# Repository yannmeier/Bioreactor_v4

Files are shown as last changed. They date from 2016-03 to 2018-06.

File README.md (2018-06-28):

# Bioreactor_v4

This repository is dedicated to the version 4 of the Bioreactor.

## Electronics

The architecture for v4 is articulated around one central board powered by 
an ATmega32u4 MCU relying on nilRTOS and external boards for interfacing
to extra sensors and/or LCD screeens.

The main board comes with the following features:
- stepper motor control with Neodimium magnet
- Load cell based on HX711
- PID heater control
- DS18B20+ temperature sensing
- LoRaWAN mid-range wireless communication
- 2 peristaltic pumps control
- SPI port to control a slave LCD board
- 2 I2C ports for master to slave communication to external modules
- Serial over USB
- 12V DC jack supply

There are already a few external extra modules:
- LCD SPI slave board on ATmega32u4
- pH & Conductommetry regulation I2C slave, also works as a stand alone (in development phase)
- gas flux and mix control with analogic valves, also works as a stand alone (in development phase)
- spectrophotometer immersed in the bioreactor, also works as a stand alone (in development phase)

References:
-https://www.arduino.cc/en/Main/ArduinoBoardLeonardo
-https://github.com/greiman/NilRTOS-Arduino

Revision notes:
Bioreactor V4.2:
- Changed operating frequency from 16MHz to 8MHz
- Changed operating voltage from 5V to 3.3V
- Removed 5V regulation
- Routed LoRa RST pin to MCU with additionnal pull-up
- Hack to be performed on hardware (D6<>D12) for software compatibility
Bioreactor V4.3:
- Stepper motor has individually controllable phases
- LoRa SMA PCB edge Antenna support
- Hack to be performed on hardware (D6<>D12) for software compatibility
Bioreactor V4.4:
- D6<>D12 exchanged to provide PWM PID control of the heater

## Mechanics

(Documentation coming soon)

#Bioreactor_v5

In parallel to the development of the version 4 of the Bioreactor, a version 5, relying on the 
more powerful SAMD21 (Cortex M0+ ARM) MCU and FreeRTOS is currently being studied.

References:
-https://www.arduino.cc/en/Main/ArduinoBoardZero
-http://www.freertos.org/Atmel_SAMD20_RTOS.html
-https://www.kickstarter.com/projects/rabidprototypes/neutrino-the-tiny-32-bit-arduino-zero-compatible/updates

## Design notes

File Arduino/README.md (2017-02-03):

# Installation

## Cloning the project

You know with age we take some habits and it would be easier if you follow the same one ...

All our github projects are always in a folder called `git`
that is at the first level of the home directory. It is followed by the 
name of the github user/organisation and finaly the project.

So to install the project from bash:
```
mkdir -p ~/git/bioreactor/
cd ~/git/bioreactor/
git clone git@github.com:Bioreactor/Bioreactor_v4.git
```

The possiblity to clone the project will require that you have validate your public key
in github !

## Installing the Arduino IDE

Currently we are still using the Arduino IDE. Plase download the last 1.6 version
of the program from: https://www.arduino.cc/en/Main/Software

## Another IDE ...

Ready to try a new IDE to program the Arduino ? Have a look at this eclipse project and install it:
http://eclipse.baeyens.it/

Once it works, start the program, select the Arduino Leonardo and go in the menu `Arduino` -> `New sketch`.
As project name just enter 'BioMain' and for the location: `~/git/bioreactor/Bioreactor_v4/Arduino/BioMain`

After don't select any template (just normal .ino files that are already in the folder). The program
will automatically import the libraries if there are placed correctly (see just after).

## Hardware support for Leonardo 8MHz = Lilipad Arduino USB

The version 4.2 of the bioreactor is opeerating at 8MHz/3V3 instead of the standard 16MHz/5V.
In order to have the correct boadloader just use Lilipad Arduino USB as board.

If you do any mistake and try to pretend it is a normal Leonardo, you will be able to flash the program but the USB port will not be recognized. You will have to reflash the bootleader !!!```

## Using USBtiny
By default the last version of Fedora will only give you a USB readonly access and will prevent to burn the board loader.
In order for the USBTiny to have r/w access you should add a USB rules:
```
# UDEV rule for Arduino ISP R3 programmer board,
# to prevent having to run Arduino IDE as root to get it to program.
# Copy this file to /etc/udev/rules.d so

SUBSYSTEMS=="usb", ATTRS{idVendor}=="1781", ATTRS{idProduct}=="0c9f", GROUP="plugdev", MODE="0666"

```

## Libraries

In this project we use many non standard libraries. By default the Arduino IDE
will look for them in `~/Arduino/libraries`

If you are using only our project it is easier to directly point this folder
to the libraries that are present in the github. 

```
mkdir ~/Arduino/
ln -s ~/git/bioreactor/Bioreactor_v4/Arduino/libraries/ ~/Arduino/
```
Attention: Time library update v1.5.0 change commited in BioMain including TimeLib.h instead of Time.h resolves bugs on OSX 

## That's it

You should now be able to compile the project from the Arduino IDE.
You can now proceed burning the bootloader using the Leonardo 8MHz newly created option and upload your code selecting the same Leonardo 8MHz in the list of available MCUs from the IDE. To do so, you must select the Leonardo 8MHz board under /Tools/Boards/ in the Arduino IDE or selecting the proper device during project creation in Eclipse. Note that the LCD board works under 16MHz/5V and must be flashed as a standard Leonardo board not a 8MHz one. You must also select the right board version when programming the board via USB !

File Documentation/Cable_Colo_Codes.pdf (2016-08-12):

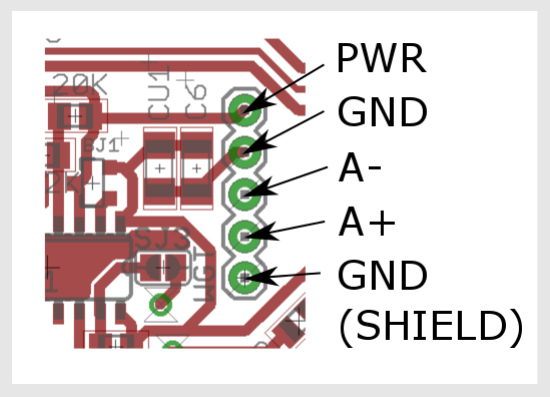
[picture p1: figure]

SENSOR
1 red | PWR (N$5)
2 black | GND
3 white | A-
4 green | A+
5 | GND (Shield)

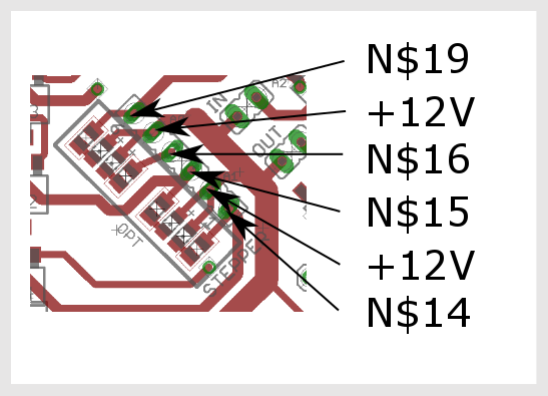
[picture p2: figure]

MOTOR
1 red | N$14
2 black | +12V
3 white | N$15
4 green | N$16
5 blue | +12V
6 yellow | N$19

## Color codes

## Load cells

MOTHERBOARD

## Stepper

MOTHERBOARD

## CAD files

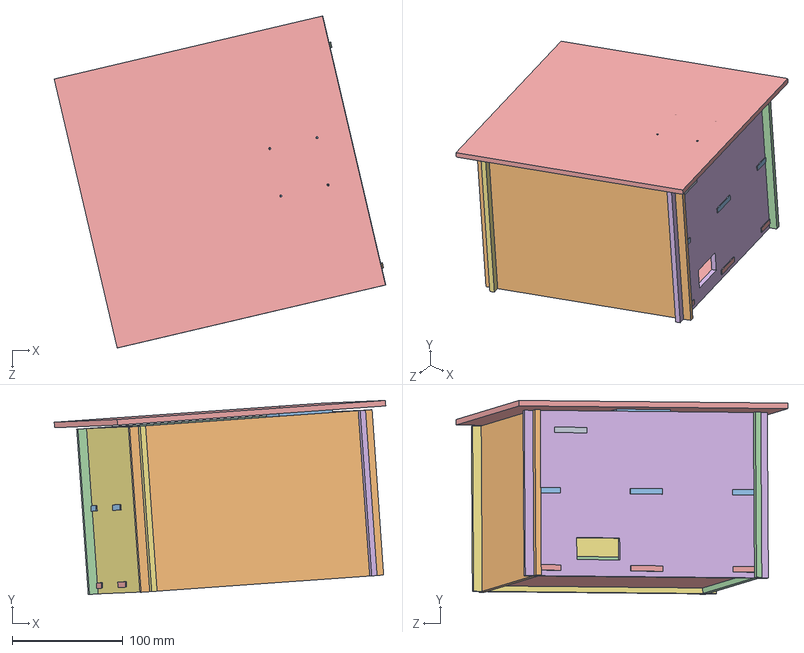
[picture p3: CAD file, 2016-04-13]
CAD/Assembly.SLDASM
300.1 x 175.7 x 300.5 mm
weight sensor
Stepper 33
middle face
Arduino
bottom face
lateral face - hole
lateral face
back support weight sensor x 2
support weight sensor
back face
support plateau
magnet support

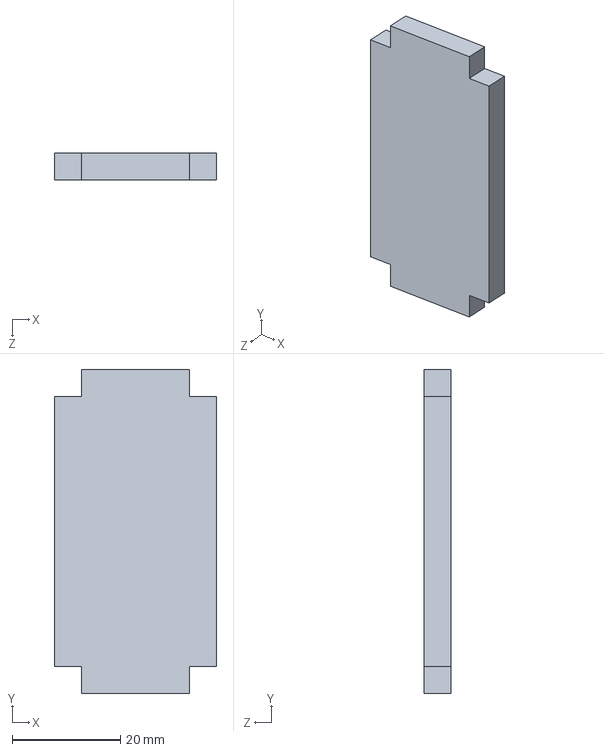
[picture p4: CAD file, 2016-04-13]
CAD/back support weight sensor.SLDPRT
30.0 x 60.0 x 5.00 mm

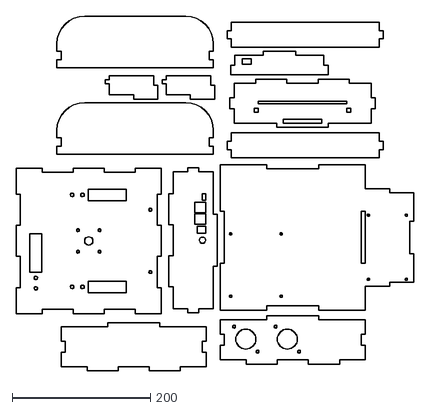
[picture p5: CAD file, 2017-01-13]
CAD/v4.3/DXF/Bioreacteur_v4_6mm.dxf
575.0 x 513.0

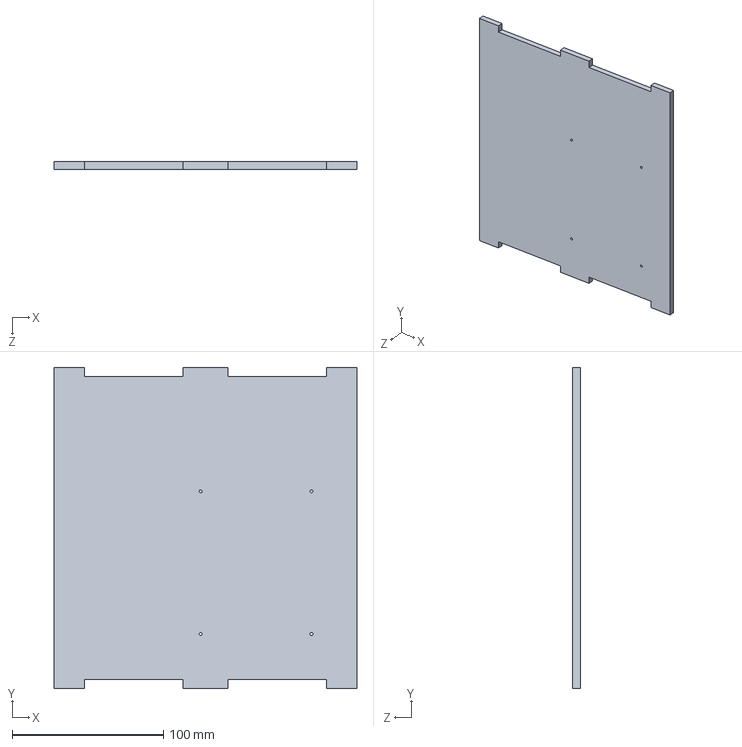
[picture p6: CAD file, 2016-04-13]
CAD/bottom face.SLDPRT
200.0 x 212.0 x 5.00 mm

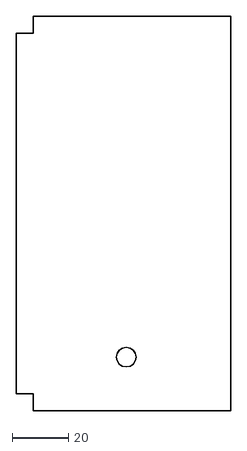
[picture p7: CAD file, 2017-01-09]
CAD/v4.3/DXF/Bioreacteur_v4_4mm.dxf
76.0 x 140.0

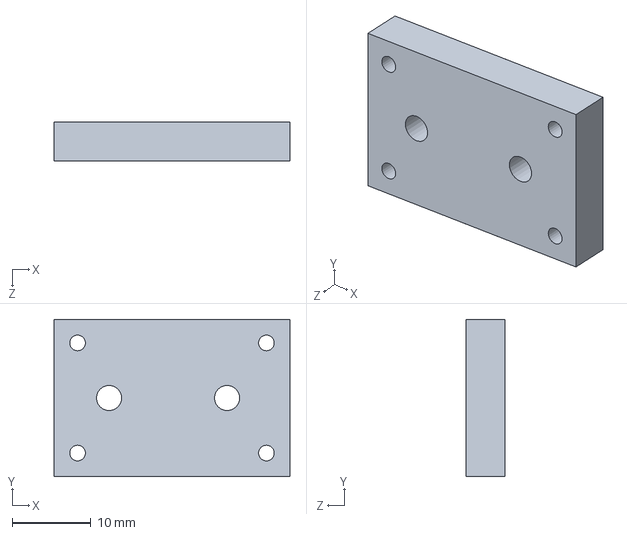
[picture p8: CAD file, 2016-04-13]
CAD/support plateau.SLDPRT
30.0 x 20.0 x 5.00 mm

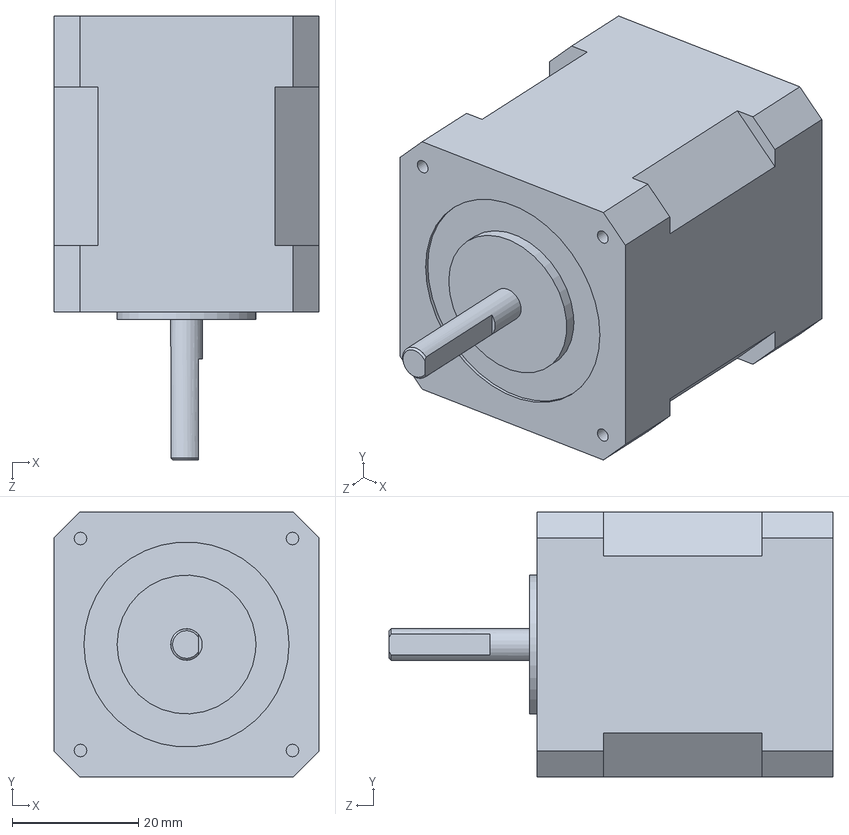
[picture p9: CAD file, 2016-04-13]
CAD/Stepper 47.SLDPRT
42.0 x 42.0 x 70.3 mm

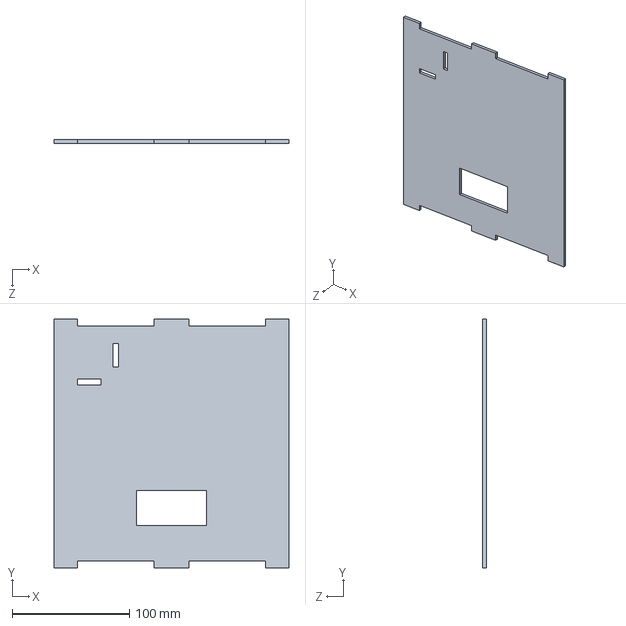
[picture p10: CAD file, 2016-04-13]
CAD/middle face.SLDPRT
200.0 x 212.0 x 3.00 mm

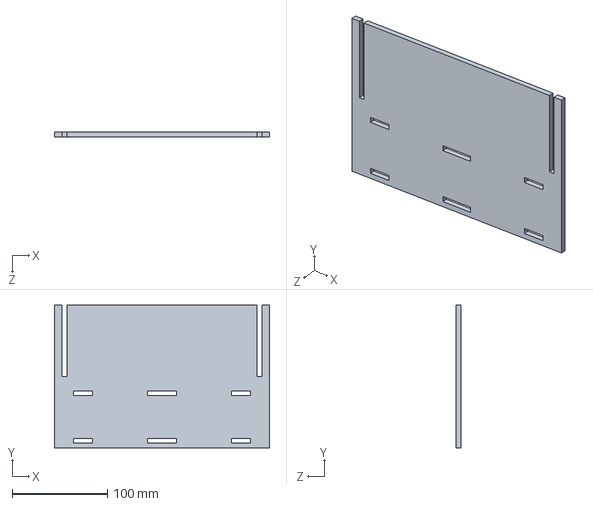
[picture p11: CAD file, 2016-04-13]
CAD/side face.SLDPRT
226.0 x 150.0 x 5.00 mm

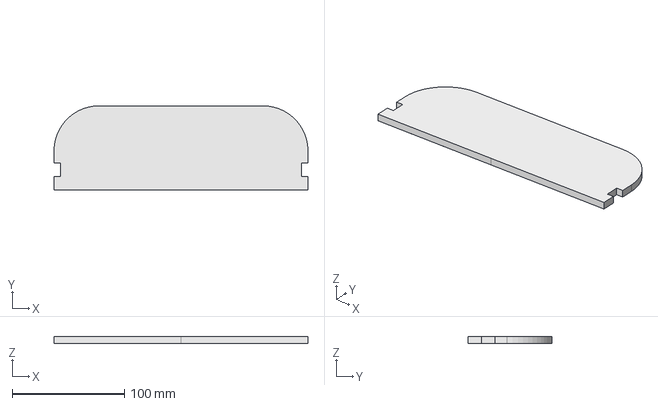
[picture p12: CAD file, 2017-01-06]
CAD/v4.3/BASE_JUPE_MALE.fcstd
226.0 x 75.0 x 6.00 mm

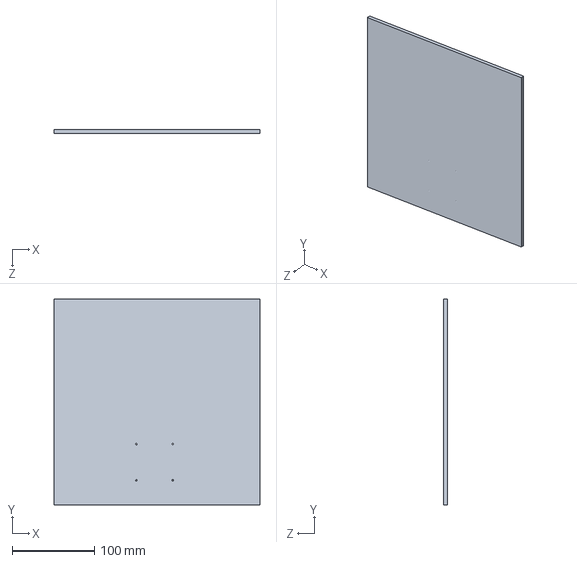
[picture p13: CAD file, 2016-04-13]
CAD/top face.SLDPRT
250.0 x 250.0 x 5.00 mm

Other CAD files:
CAD/v4.3/Tank_alu_foundation.FCStd
CAD/v4.3/Bioreactor_sketches_04.fcstd
CAD/v4.3/Bioreactor_sketches_03.fcstd
CAD/v4.3/Bioreactor_sketches.fcstd
CAD/v4.3/Bioreactor_sketches_02.fcstd
CAD/Arduino.SLDPRT
CAD/Stepper 33.SLDPRT
CAD/back face.SLDPRT
CAD/front face.SLDPRT
CAD/lateral face - hole.SLDPRT
CAD/lateral face.SLDPRT
CAD/magnet support.SLDPRT
CAD/support weight sensor.SLDPRT
CAD/v4.0_old/back face.SLDPRT
CAD/v4.0_old/front face.SLDPRT
CAD/v4.0_old/lateral face - hole.SLDPRT
CAD/v4.0_old/lateral face.SLDPRT
CAD/v4.0_old/magnet support.SLDPRT
CAD/v4.0_old/support weight sensor.SLDPRT
CAD/v4.1/A Bioreactor v3.SLDASM
CAD/v4.1/A screen.SLDASM
CAD/v4.1/Box Board v1.4.stl
CAD/v4.1/Foot.SLDPRT
CAD/v4.1/Pump support v1.2 .stl
CAD/v4.1/Pump support.SLDPRT
CAD/v4.1/Screen support v1.1.SLDPRT
CAD/v4.1/Screen support v1.1.stl
CAD/v4.1/Screen support.STL
CAD/v4.1/Support v3.1.SLDPRT
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

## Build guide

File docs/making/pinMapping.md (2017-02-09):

Pin mapping
===========

Port | Pin | Arduino Mask | Bertha V4.1-2 | Bertha V4.3 | Bertha V4.4 | pH V5.x | LCD V0.2/V1.x
-----|-----|--------------|---------------|-------------|-------------|---------|---------------
B | 0 | RXLED/SS | RXLED | RXLED | RXLED | RXLED | SS
B | 1 | SCK | SCK | SCK | SCK | SCK | SCK
B | 2 | MOSI | MOSI | MOSI | MOSI | MOSI | MOSI
B | 3 | MISO | MISO | MISO | MISO | MISO | MISO
B | 4 | D8 | - | Stepper 1 | Stepper 1 | Stepper#1-1 | LCD #11
B | 5 | D9 | - | Stepper 2 | Stepper 2 |  | LCD #6
B | 6 | D10 | SPI flash slave | SPI flash slave | PWM food IN | SPI flash slave | LCD #4
B | 7 | D11 | SPI LCD slave | SPI LCD slave | SPI LCD slave | SPI LCD slave | -
C | 6 | D5 | LoRa RST | LoRa RST | PWM food OUT | LoRa RST | -
C | 7 | D13 | Blink Led | Blink Led | Blink Led | Blink Led | Blink Led
D | 0 | D3/SCL | I2C SCL | I2C SCL | I2C SCL | I2C SCL | -
D | 1 | D2/SDA | I2C SDA | I2C SDA | I2C SDA | I2C SDA | -
D | 2 | D0/RX | LoRa RX | LoRa RX | LoRa RX | LoRa RX | ENC B
D | 3 | D1/TX | LoRa TX | LoRa TX | LoRa TX | LoRa TX | ENC A
D | 4 | D4/A6 | Ext. OneWire | Ext. OneWire | Ext. OneWire | Stepper#1-2 | LCD #14
D | 5 | TXLED | TXLED | TXLED | TXLED | TXLED | -
D | 6 | D12 | PID (hack: D12<>D6) | PID (hack: D12<>D6) | OneWire | Stepper#1-3 | LCD #13
D | 7 | D6 | OneWire (hack: D6<>D12) | OneWire (hack: D6<>D12) | PID on PWM | Stepper#1-4 | LCD #12
E | 2 | D7 | - | - | - | Data HX711 | ENCODER INT
E | 6 | HWB | HWB | HWB | HWB | HWB | HWB
F | 0 | A5 | SCK HX711 | SCK HX711 | SCK HX711 | SCK HX711 | -
F | 1 | A4 | Data HX711 | Data HX711 | Data HX711 | PH NTC TEMP | -
F | 4 | A3 | Food out | Food out | SPI flash slave | Stepper#2-4 | -
F | 5 | A2 | Food in | Food in | LoRa RST | Stepper#2-1 | -
F | 6 | A1 | Stepper 2+4 | Stepper 4 | Stepper 4 | Stepper#2-2 | -
F | 7 | A0 | Stepper 1+3 | Stepper 3 | Stepper 3 | Stepper#2-3 | -

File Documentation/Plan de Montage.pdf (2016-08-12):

# PLAN DE MONTAGE

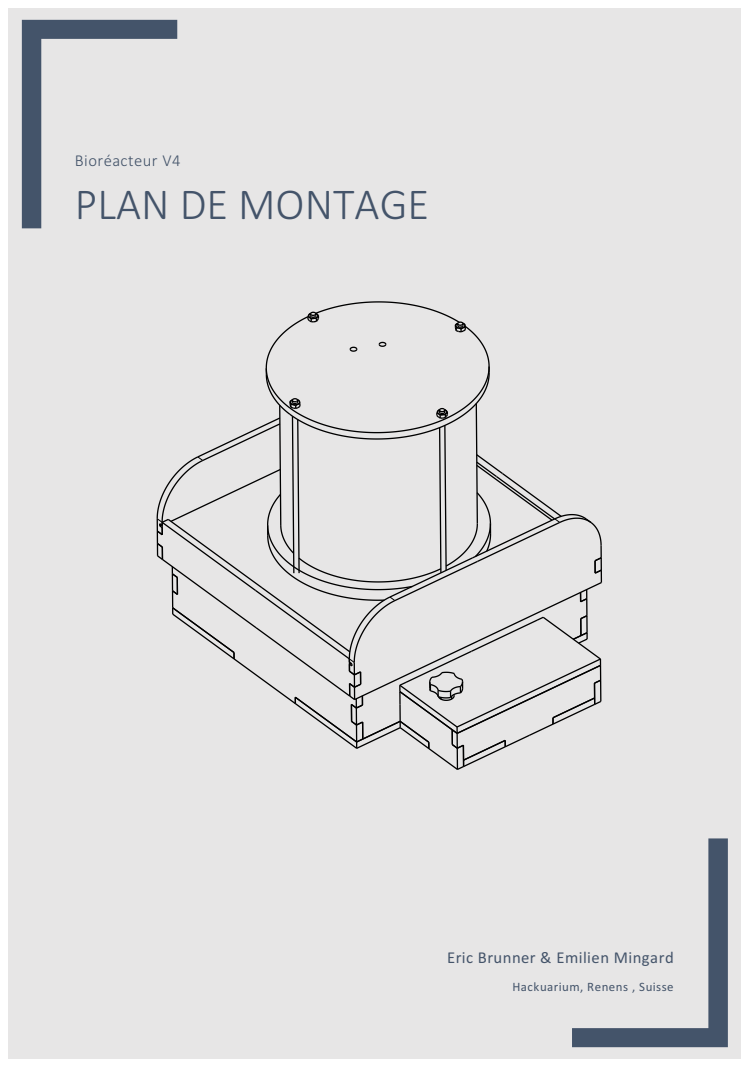
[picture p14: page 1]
Bioréacteur V4

Eric Brunner & Emilien Mingard

Hackuarium, Renens , Suisse

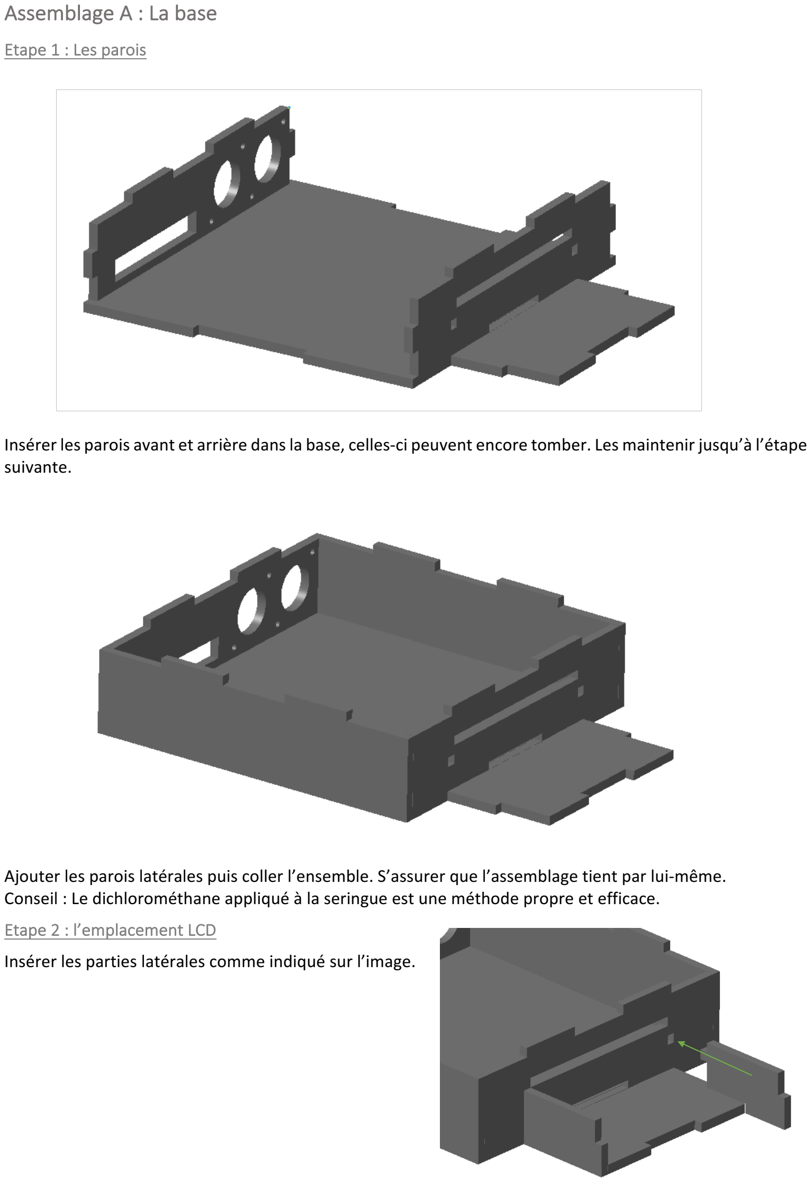
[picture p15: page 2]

### Assemblage A : La base

Etape 1 : Les parois

Insérer les parois avant et arrière dans la base, celles-ci peuvent encore tomber. Les maintenir jusqu’à l’étape suivante.

Ajouter les parois latérales puis coller l’ensemble. S’assurer que l’assemblage tient par lui-même. Conseil : Le dichlorométhane appliqué à la seringue est une méthode propre et efficace.
Etape 2 : l’emplacement LCD
Insérer les parties latérales comme indiqué sur l’image.

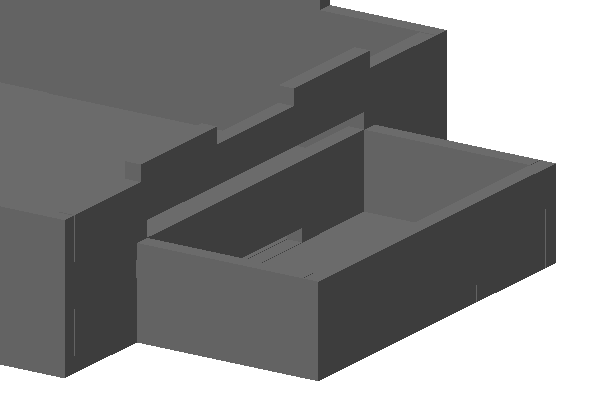
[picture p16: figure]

Déposer la partie centrale pour compléter l’espace puis coller avec de la colle. Conseil : Voir étape 1.
Etape 3 : Installation des composants électroniques et mécaniques

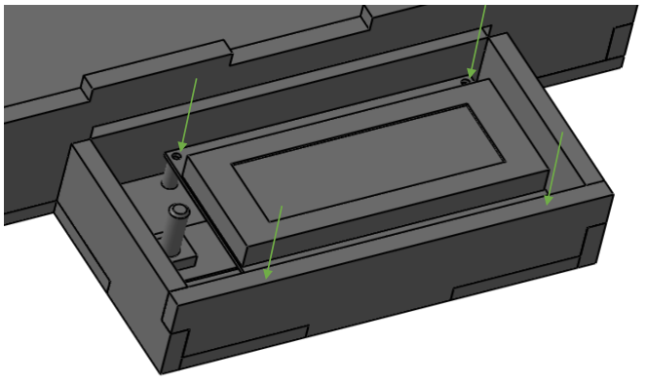
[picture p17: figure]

Visser l’écran LCD dans son emplacement, celui-ci s’appuie sur 4 entretoises 14mm. Pièces standards : 4 x M3x20.

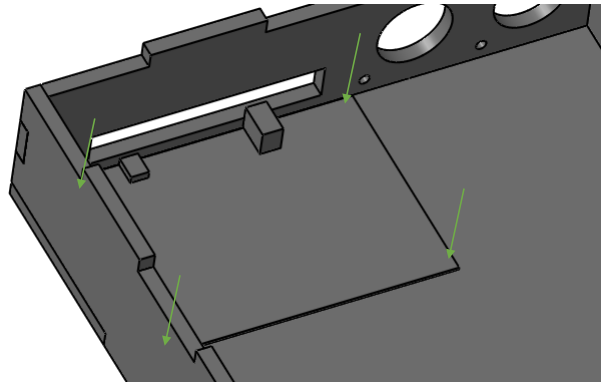
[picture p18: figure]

Visser la carte mère en face de l’ouverture prévue sur la partie arrière, les ports doivent être visibles de l’extérieur. Des entretoises de 4mm sont nécessaires.
Pièces standards : 4 x M3x10 (Solution économe : 4 x M3x20 avec entretoises supplémentaires).

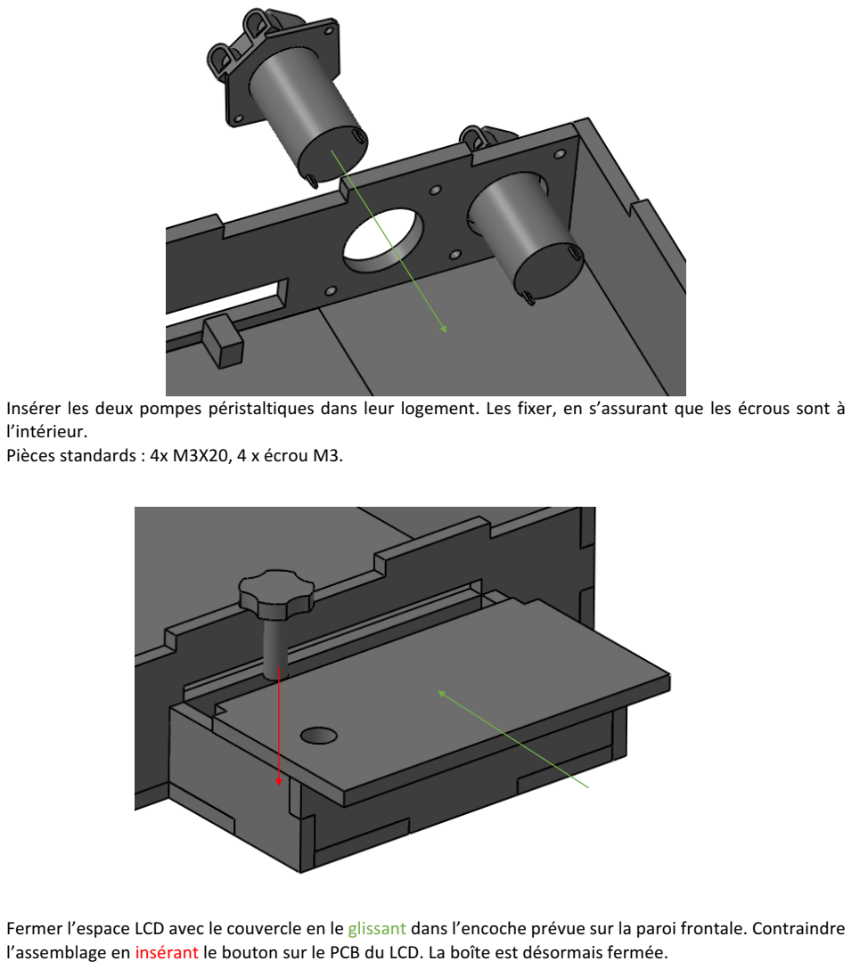
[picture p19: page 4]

Insérer les deux pompes péristaltiques dans leur logement. Les fixer, en s’assurant que les écrous sont à l’intérieur.
Pièces standards : 4x M3X20, 4 x écrou M3.

Fermer l’espace LCD avec le couvercle en le glissant dans l’encoche prévue sur la paroi frontale. Contraindre l’assemblage en insérant le bouton sur le PCB du LCD. La boîte est désormais fermée.

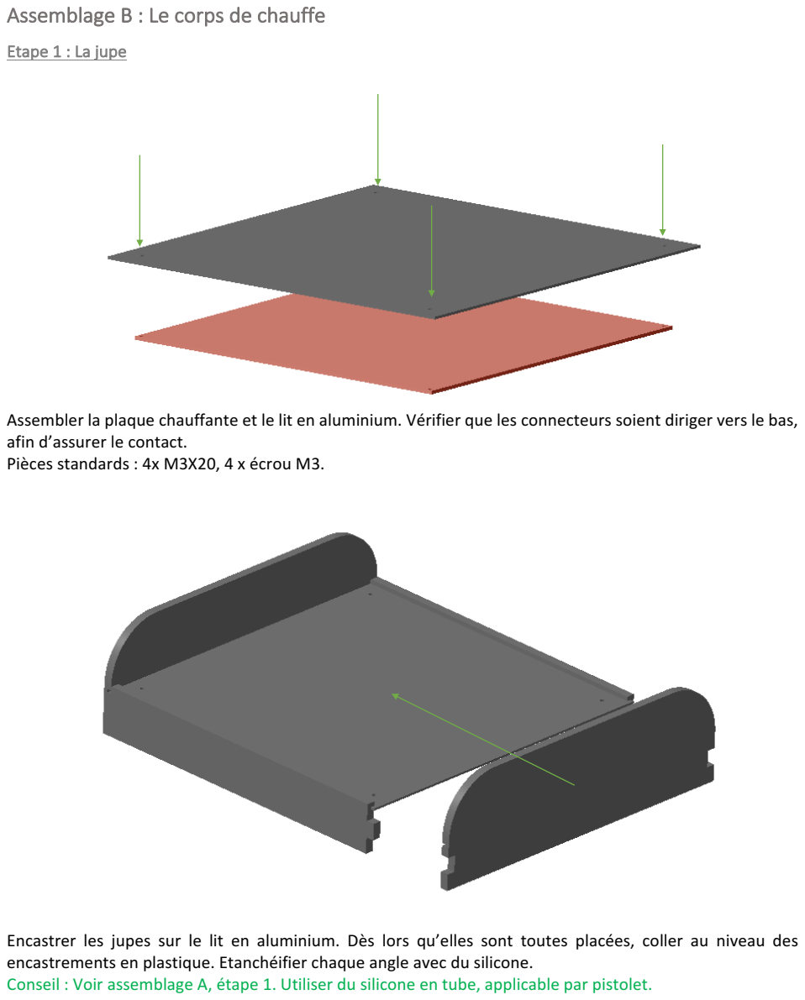
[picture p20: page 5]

### Assemblage B : Le corps de chauffe

Etape 1 : La jupe

Assembler la plaque chauffante et le lit en aluminium. Vérifier que les connecteurs soient diriger vers le bas, afin d’assurer le contact.
Pièces standards : 4x M3X20, 4 x écrou M3.

Encastrer les jupes sur le lit en aluminium. Dès lors qu’elles sont toutes placées, coller au niveau des encastrements en plastique. Etanchéifier chaque angle avec du silicone.
Conseil : Voir assemblage A, étape 1. Utiliser du silicone en tube, applicable par pistolet.

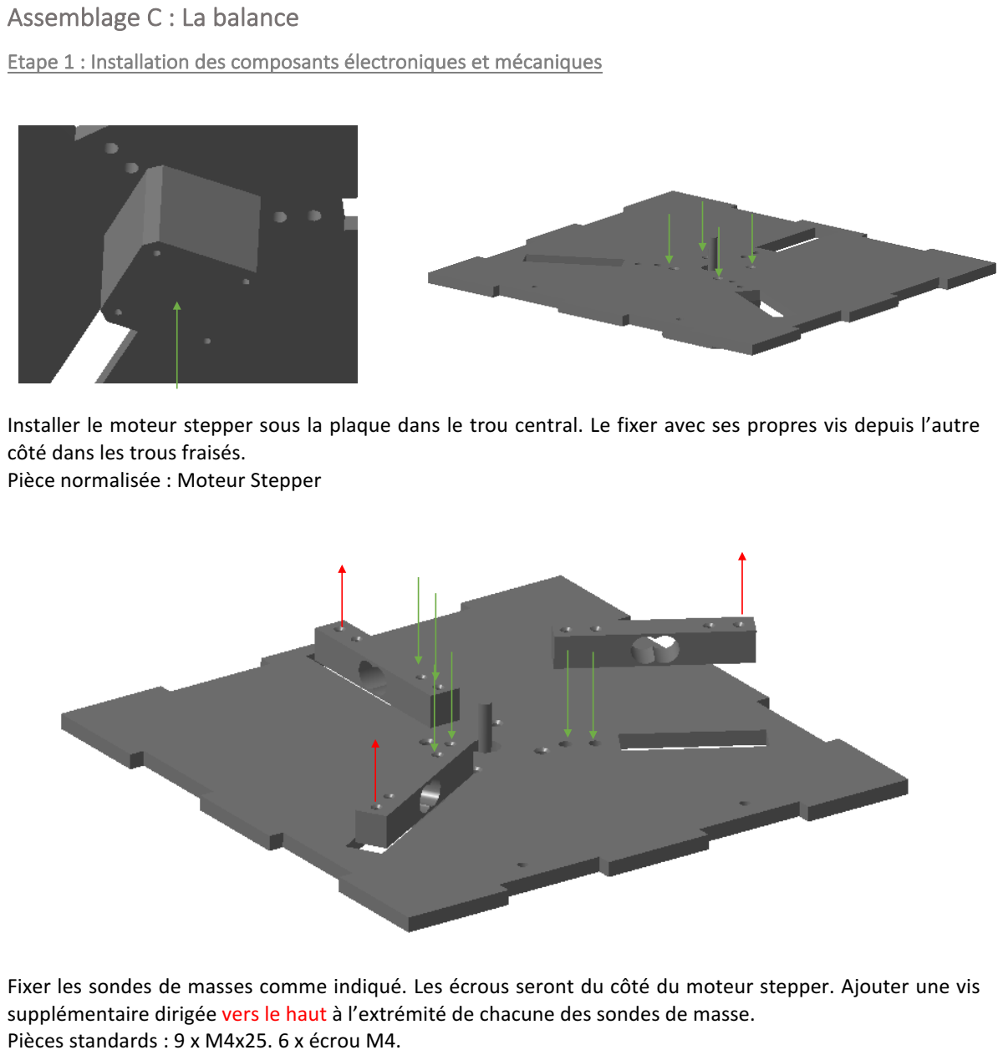
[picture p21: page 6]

### Assemblage C : La balance

Etape 1 : Installation des composants électroniques et mécaniques

Installer le moteur stepper sous la plaque dans le trou central. Le fixer avec ses propres vis depuis l’autre côté dans les trous fraisés.
Pièce normalisée : Moteur Stepper

Fixer les sondes de masses comme indiqué. Les écrous seront du côté du moteur stepper. Ajouter une vis supplémentaire dirigée vers le haut à l’extrémité de chacune des sondes de masse.
Pièces standards : 9 x M4x25. 6 x écrou M4.

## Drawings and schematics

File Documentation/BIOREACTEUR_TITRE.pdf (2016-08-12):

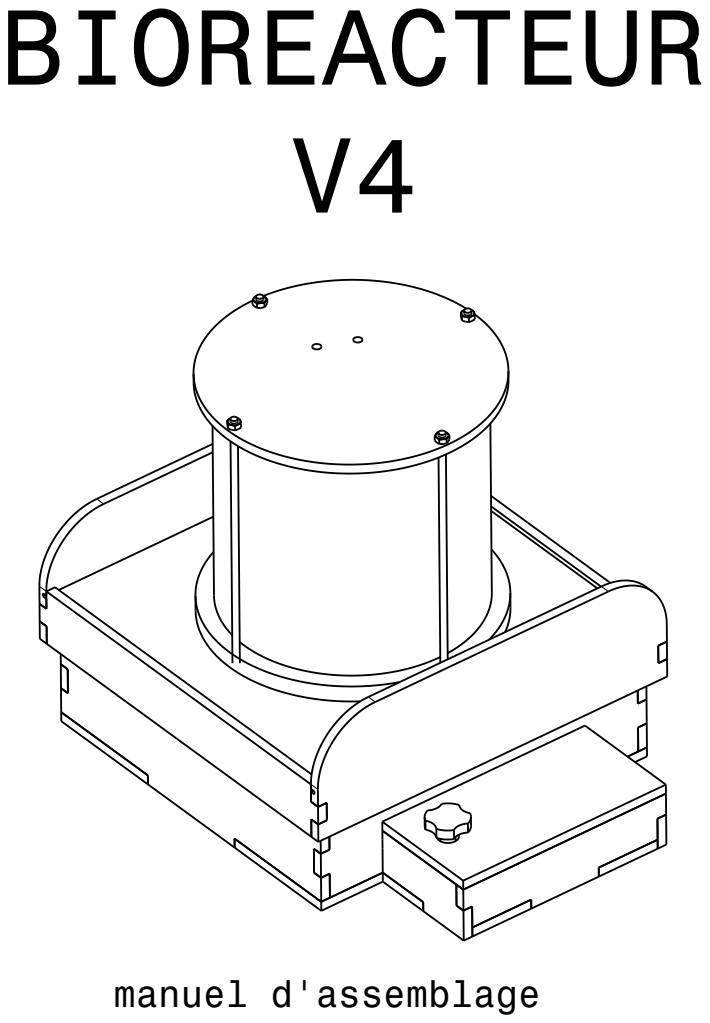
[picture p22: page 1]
manuel d'assemblage

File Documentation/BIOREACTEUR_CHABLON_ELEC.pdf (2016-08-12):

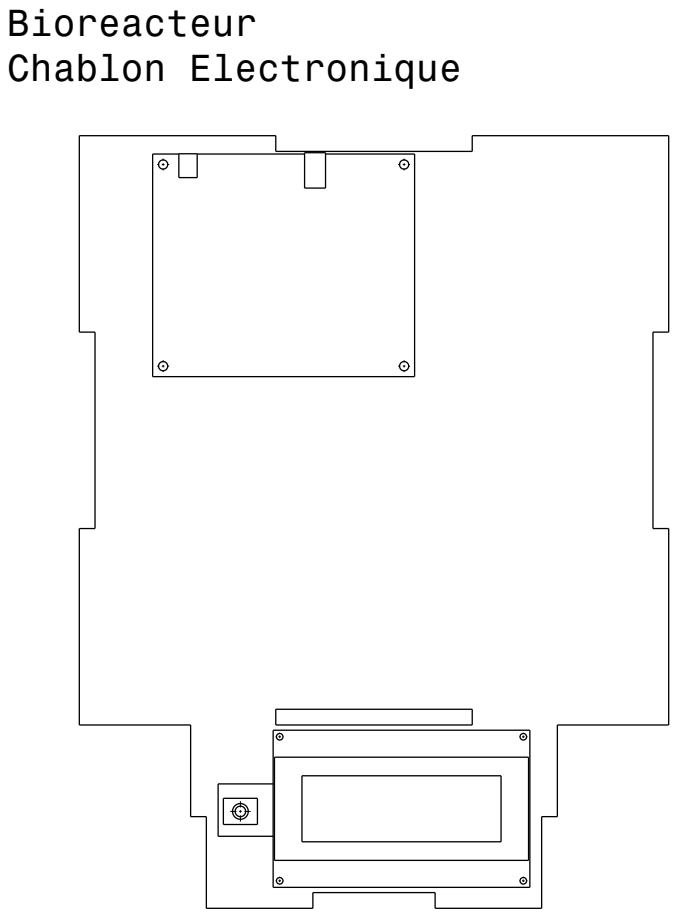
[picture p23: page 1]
Chablon Electronique

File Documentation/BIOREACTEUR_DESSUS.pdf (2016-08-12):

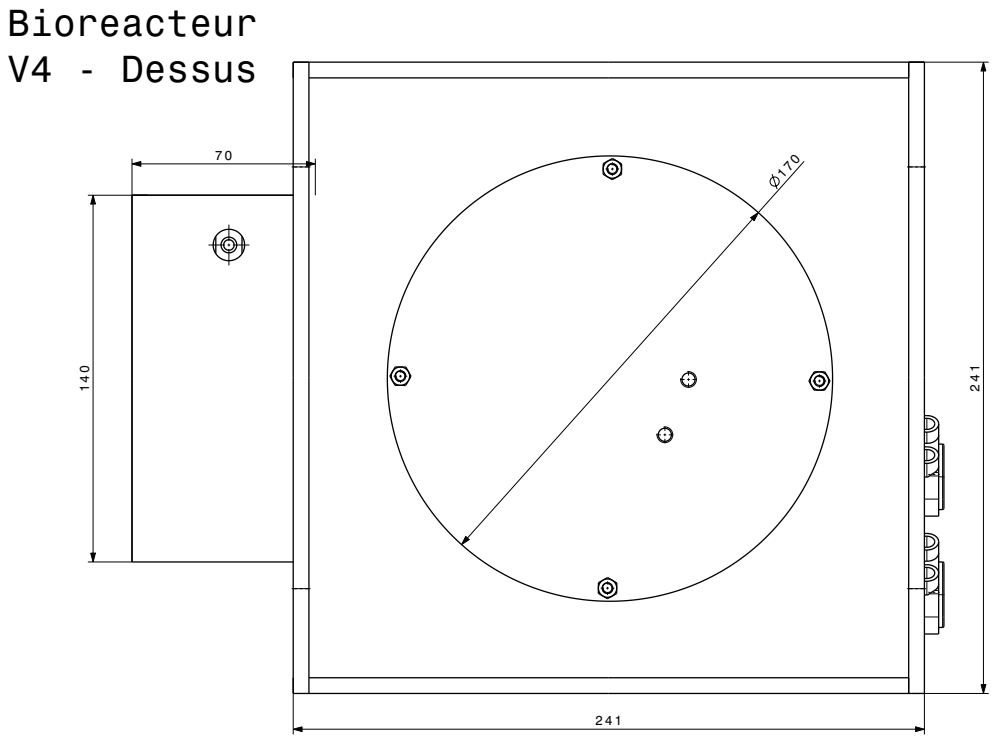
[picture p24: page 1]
V4 - Dessus

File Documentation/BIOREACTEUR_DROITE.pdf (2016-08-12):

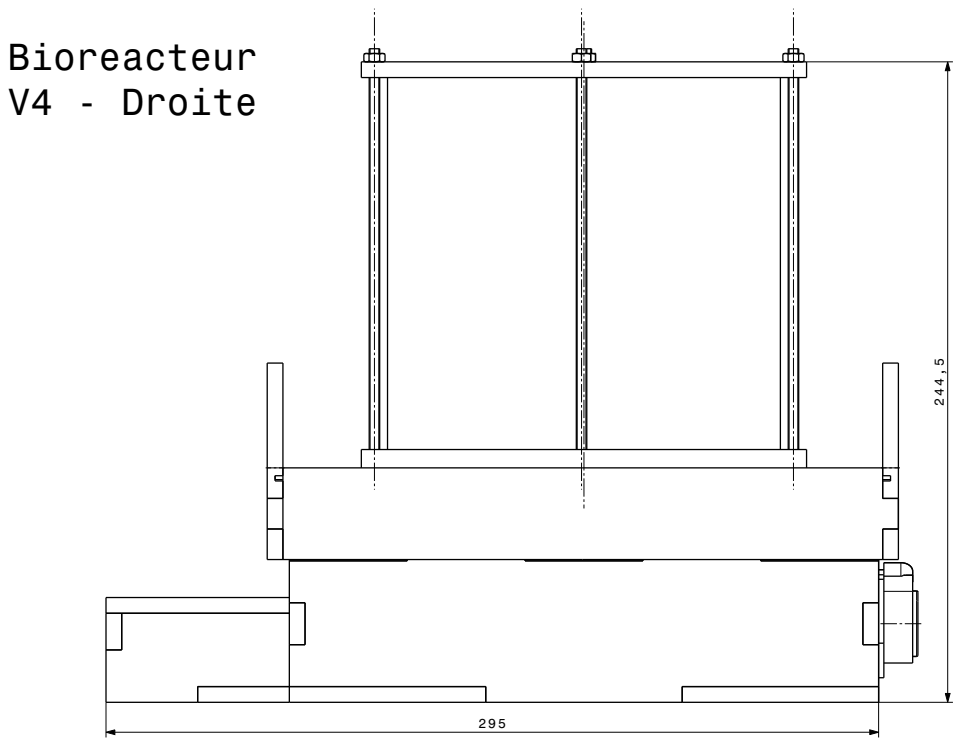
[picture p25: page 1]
V4 - Droite

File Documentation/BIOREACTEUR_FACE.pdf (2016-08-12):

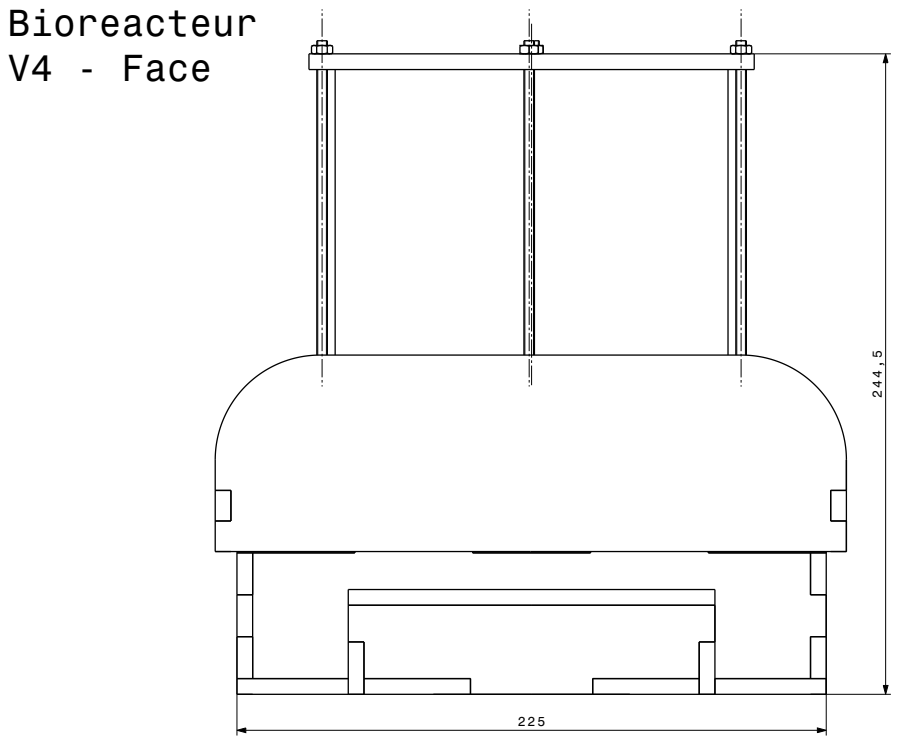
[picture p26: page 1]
V4 - Face

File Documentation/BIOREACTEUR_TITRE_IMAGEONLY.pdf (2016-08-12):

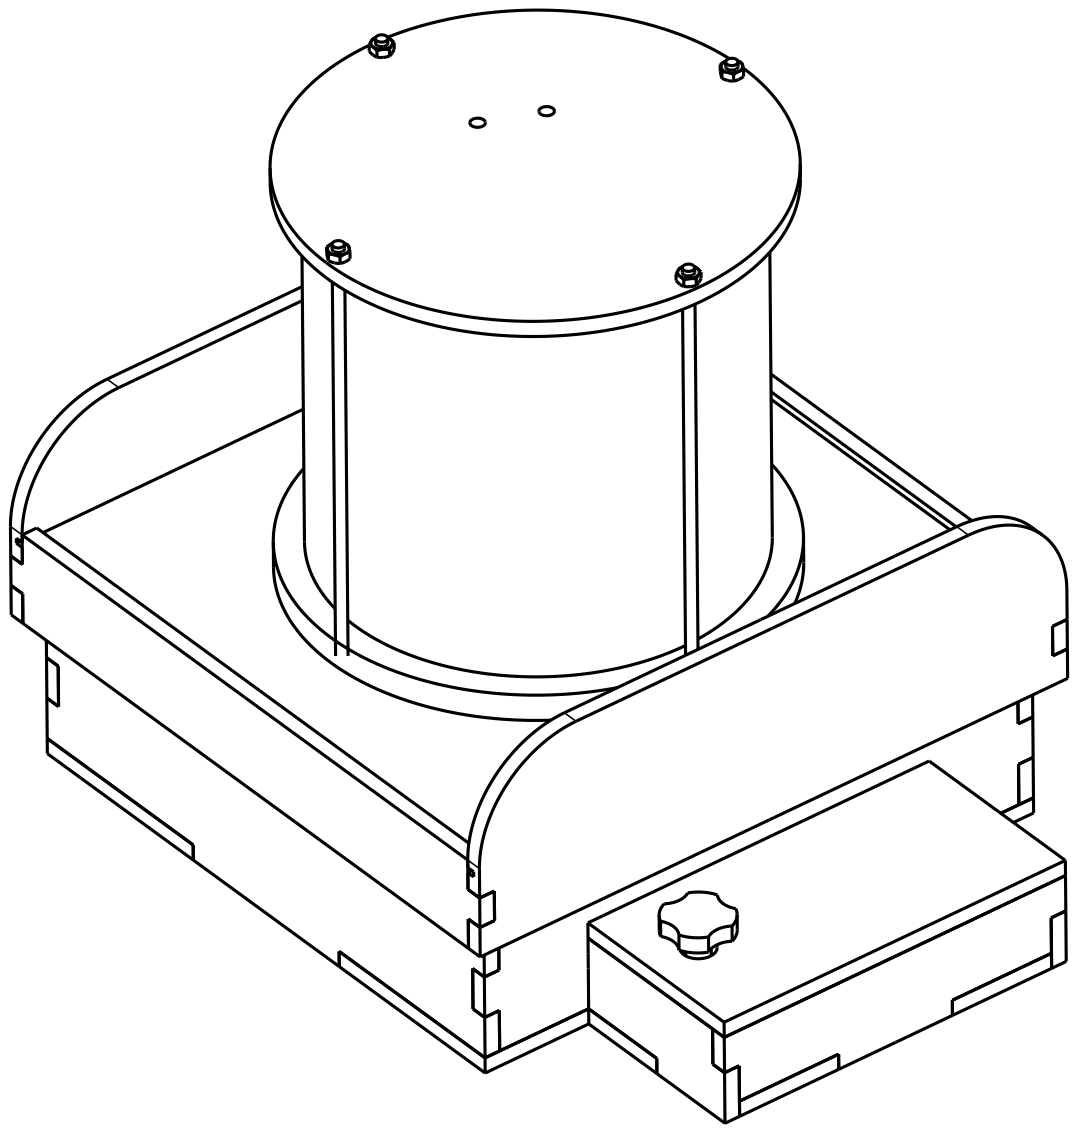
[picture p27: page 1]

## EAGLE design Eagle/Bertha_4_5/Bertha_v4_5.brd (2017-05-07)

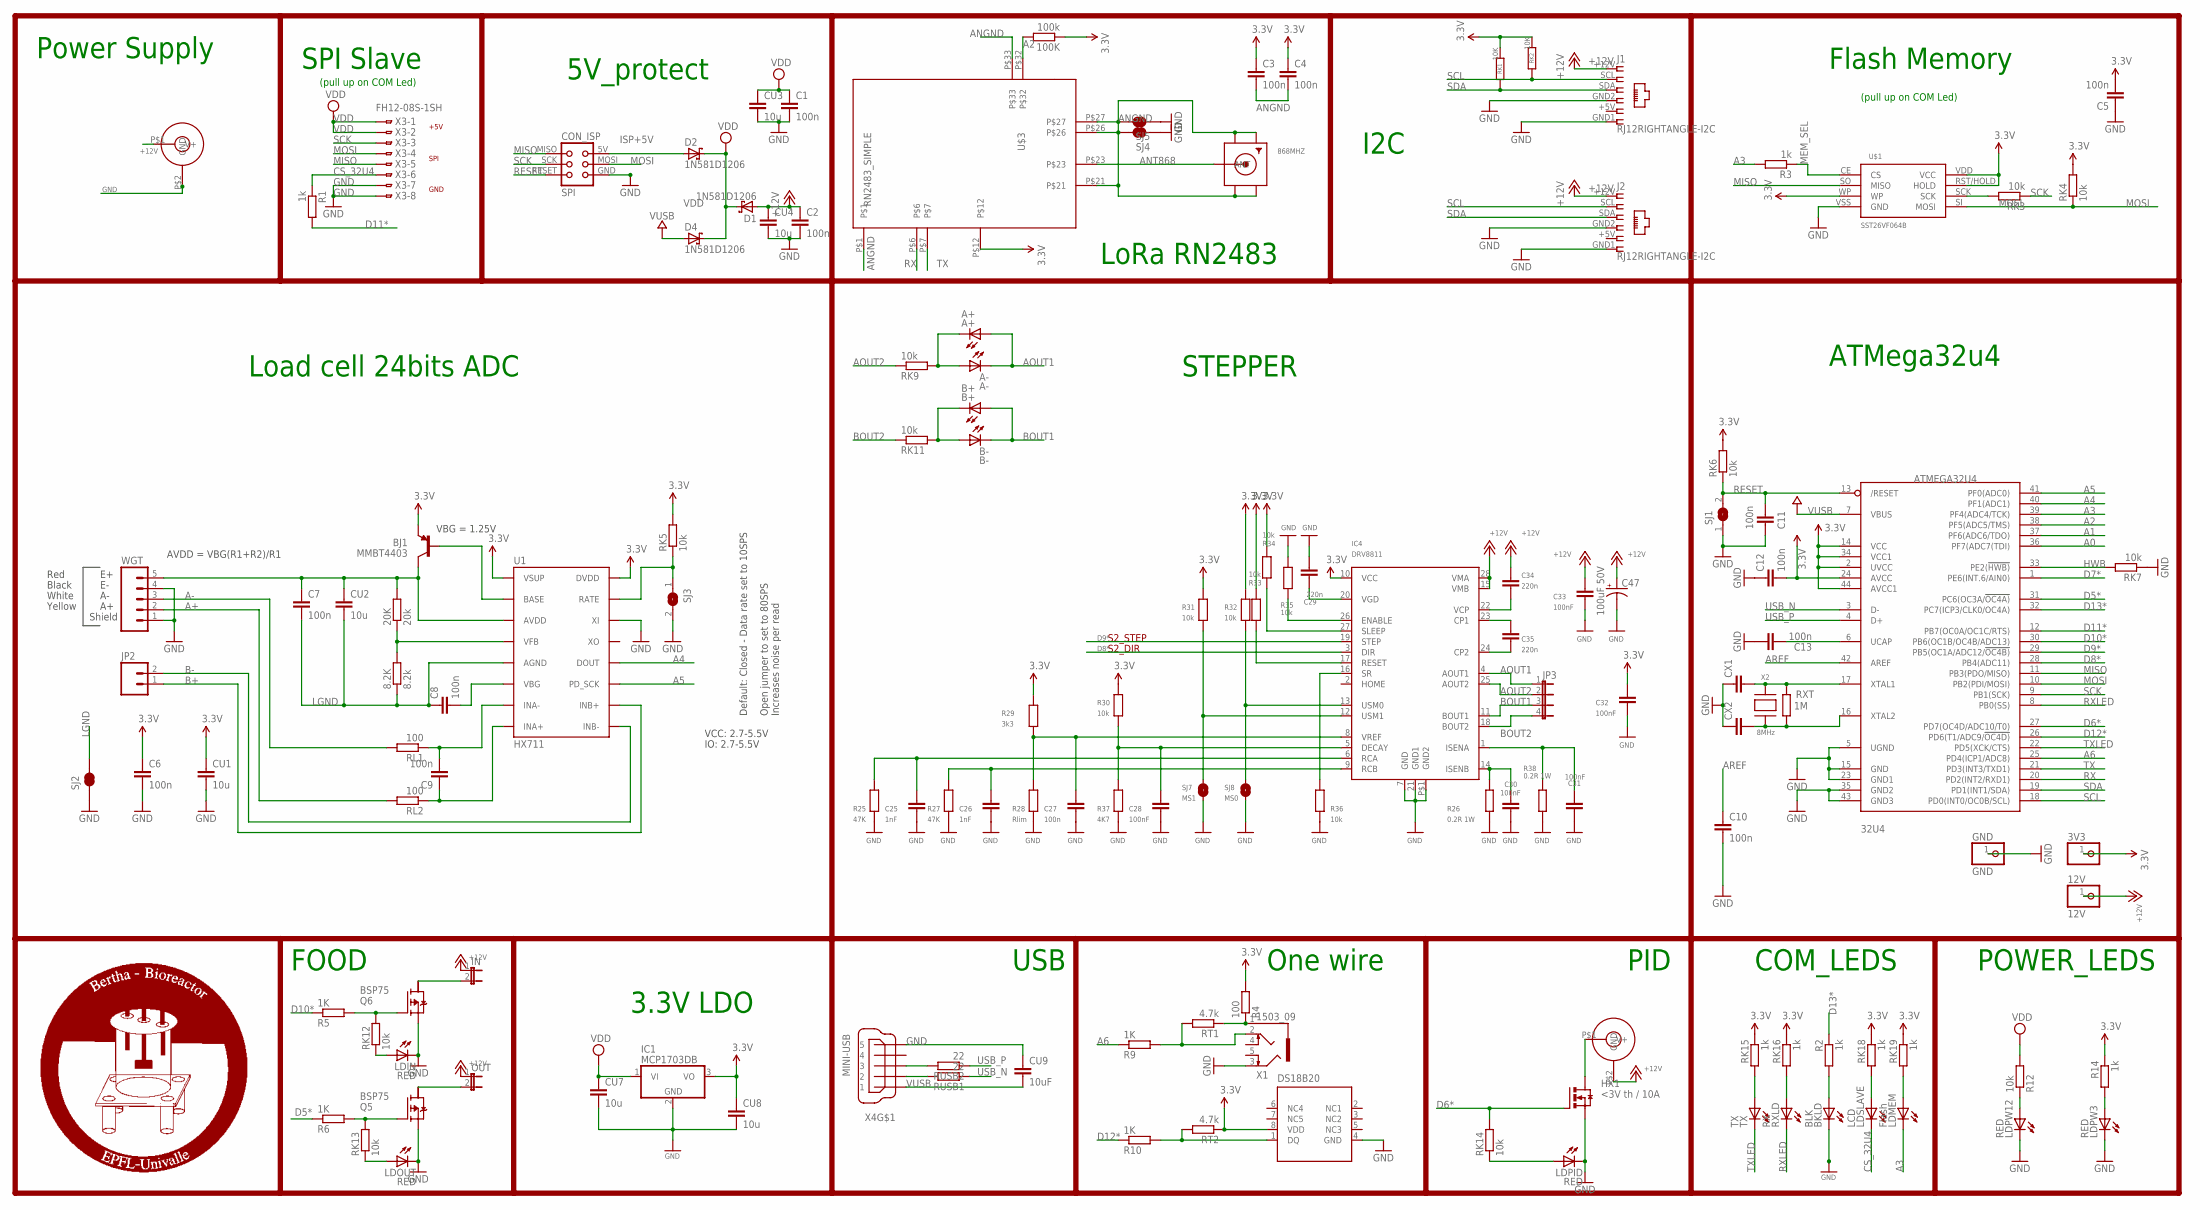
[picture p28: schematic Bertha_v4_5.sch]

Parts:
3V3: PINHD-1X1; 1X01
8.2K: 8.2k; M0805
12V: 12V; 1X01
20K: 20k; M0805
32U4: ATMEGA32U4; TQFP44
100K: 100k; R0805
868MHZ: SMACONNECTOR_EDGE_UFL; SMA_EDGELAUNCH_UFL
A+: A+; CHIP-LED0805
A-: A-; CHIP-LED0805
B+: B+; CHIP-LED0805
B-: B-; CHIP-LED0805
BJ1: MMBT4403; SOT23-3
BKLD: BLK; CHIP-LED0805
C1, C2, C3, C4, C5, C6, C7, C8, C9, C10, C11, C12, C13: 100n; C0805
C25, C26: 1nF; 0805
C27: 100n; 0805
C28, C30, C31, C32, C33: 100nF; 0805
C29, C34, C35: 220n; 0805
C47: 100uF 50V; PANASONIC_E
CON1, CON2: JACK_DC_BARREL; DC_BARREL
CON_ISP: SPI; TC2030-MCP-NL
CU1, CU2, CU3, CU4, CU7, CU8: 10u; C0805
CU9: 10uF; C0805
CX1, CX2: 22pF; C0805
D1, D2, D4: 1N581D1206; LED-1206
GND: GND; 1X01
HX1: <3V th / 10A; D2PACK
IC1: MCP1703DB; SOT223
IC4: DRV8811; HTSSOP28
IN: JP1E; JP1
J1, J2: RJ12RIGHTANGLE-I2C; RJ12-RIGHTANGLE-I2C
JP2: M02PTH; 1X02
JP3: JP4E; JP4
LDIN: RED; CHIP-LED0805
LDMEM: Flash; CHIP-LED0805
LDOUT: RED; CHIP-LED0805
LDPID: RED; CHIP-LED0805
LDPW3, LDPW12: RED; CHIP-LED0805
LDSLAVE: LCD; CHIP-LED0805
OUT: JP1E; JP1
Q5, Q6: BSP75; PG-SOT-223
R1, R2, R3, R14: 1k; R0805
R4: 100; R0805
R5, R6, R9, R10: 1K; R0805
R12: 10k; R0805
R25, R27: 47K; 0805
R26, R38: 0.2R 1W; R2010
R28: Rlim; 0805
R29: 3k3; 0805
R30, R31, R32, R33, R34, R35, R36: 10k; 0805
R37: 4K7; 0805
RK1, RK2: 10K; M0805
RK3, RK4, RK9, RK11, RK12, RK13, RK14: 10k; R0805
RK5, RK6, RK7: 10k; M0805
RK15, RK16, RK18, RK19: 1k; R0805
RL1, RL2: 100; M0805
RT1, RT2: 4.7k; R0805
RUSB1, RUSB2: 22; M0805
RXLD: RX; CHIP-LED0805
RXT: 1M; R0805
SJ1, SJ3: SJ
SJ2, SJ4, SJ5: JUMPER-PAD-2-NC_BY_TRACE; PAD-JUMPER-2-NC_BY_TRACE_YES_SILK
SJ7: MS1; SJ
SJ8: MS0; SJ
TX: TX; CHIP-LED0805
U1: HX711; SO16
U$1: SST26VF064B; SOIC_8-LEAD
U$2: DS18B20; MSOP8
U$3: RN2483_SIMPLE
WGT: M05PTH; 1X05
X1: 1503_09
X2: 8MHz; NX6035
X3: FH12-08S-1SH
X4: MINI-USB; 32005-201

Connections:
3.3V: 3V3.1, 32U4.2 (UVCC), 32U4.14 (VCC), 32U4.24 (AVCC), 32U4.34 (VCC1), 32U4.44 (AVCC1), 100K.1, BJ1.2 (E), C3.1, C4.1, C5.2, C6.1, C12.2, C32.1, CU1.1, CU8.1, IC1.3 (VO), IC4.10 (VCC), R4.2, R14.1, R29.2, R30.2, R31.2, R32.2, R33.2, R34.2, RK1.1, RK2.1, RK4.2, RK5.2, RK6.2, RK15.1, RK16.1, RK18.1, RK19.1, RT2.1, U1.1 (VSUP), U1.16 (DVDD), U$1.RST/HOLD (HOLD), U$1.VDD (VCC), U$1.WP, U$2.8 (VDD), U$3.P$12
5: J1.+5V (5), J2.+5V (5)
+12V: 12V.1, C2.1, C33.1, C34.1, C47.+, CON1.P$1 (V+), CON2.P$2 (GND), CU4.1, D1.A, IC4.15 (VMB), IC4.28 (VMA), IN.1, J1.+12V (1), J2.+12V (1), OUT.1
A0: 32U4.36 (PF7(ADC7(TDI))
A1: 32U4.37 (PF6(ADC6/TDO))
A2: 32U4.38 (PF5(ADC5/TMS)), 100K.2, U$3.P$32
A3: 32U4.39 (PF4(ADC4/TCK)), LDMEM.C, R3.2
A4: 32U4.40 (PF1(ADC1)), U1.12 (DOUT)
A5: 32U4.41 (PF0(ADC0)), U1.11 (PD_SCK)
A6: 32U4.25 (PD4(ICP1/ADC8)), R9.1
A+: RL2.2, WGT.2
A-: RL1.2, WGT.3
ANGND: 868MHZ.GND@1 (GND1), 868MHZ.GND@2 (GND2), 868MHZ.GND@3 (GND3), 868MHZ.GND@4 (GND4), C3.2, C4.2, SJ4.2, SJ5.2, U$3.P$1, U$3.P$21, U$3.P$26, U$3.P$27, U$3.P$33
ANT868: 868MHZ.P (ANT), U$3.P$23
AOUT1: A+.A, A-.C, IC4.4 (AOUT1), JP3.1
AOUT2: IC4.25 (AOUT2), JP3.2, RK9.1
AREF: 32U4.42 (AREF), C10.1
B+: JP2.1, U1.10 (INB+)
B-: JP2.2, U1.9 (INB-)
BOUT1: B+.A, B-.C, IC4.11 (BOUT1), JP3.3
BOUT2: IC4.18 (BOUT2), JP3.4, RK11.1
CN3: C8.2, U1.6 (VBG)
CS_32U4: LDSLAVE.C, R1.1, X3.6
D5*: 32U4.31 (PC6(OC3A/!OC4A)), R6.1
D6*: 32U4.27 (PD7(OC4D/ADC10/T0)), HX1.1 (G), RK14.2
D7*: 32U4.1 (PE6(INT.6/AIN0))
D8*: 32U4.28 (PB4(ADC11)), IC4.3 (DIR)
D9*: 32U4.29 (PB5(OC1A/ADC12/!OC4B)), IC4.19 (STEP)
D10*: 32U4.30 (PB6(OC1B/OC4B/ADC13)), R5.1
D11*: 32U4.12 (PB7(OC0A/OC1C/RTS)), R1.2
D12*: 32U4.26 (PD6(T1/ADC9/!OC4D)), R10.1
D13*: 32U4.32 (PC7(ICP3/CLK0/OC4A)), R2.1
GND: 32U4.5 (UGND), 32U4.15 (GND), 32U4.23 (GND1), 32U4.35 (GND2), 32U4.43 (GND3), BKLD.C, C1.2, C2.2, C5.1, C6.2, C10.2, C11.2, C12.1, C13.1, C25.2, C26.2, C27.2, C28.2, C29.2, C30.2, C31.2, C32.2, C33.2, C47.-, CON1.P$2 (GND), CON_ISP.GND, CU1.2, CU3.2, CU4.2, CU7.2, CU8.2, CU9.1, CX1.1, CX2.1, GND.1, HX1.3 (S), IC1.2 (GND), IC4.7 (GND), IC4.21 (GND1), IC4.P$1 (GND2), J1.GND1 (6), J1.GND2 (4), J2.GND1 (6), J2.GND2 (4), LDIN.C, LDOUT.C, LDPID.C, LDPW3.C, LDPW12.C, Q5.3 (S), Q6.3 (S), R25.1, R26.1, R27.1, R28.1, R35.1, R36.1, R37.1, R38.1, RK7.1, SJ1.1, SJ2.1, SJ3.2, SJ4.1, SJ5.1, SJ7.1, SJ8.1, U1.14 (XI), U$1.VSS (GND), U$2.4 (GND), WGT.1, WGT.4, X1.3, X3.7, X3.8, X4.5
HWB: 32U4.33 (PE2(!HWB)), RK7.2
ISP+5V: CON_ISP.5V (VCC), D2.A
LGND: 8.2K.1, C7.2, C8.1, CU2.2, SJ2.2, U1.5 (AGND)
MEM_SEL: R3.1, U$1.CE (CS)
MISO: 32U4.11 (PB3(PDO/MISO)), CON_ISP.MISO, U$1.SO (MISO), X3.5
MOSI: 32U4.10 (PB2(PDI/MOSI)), CON_ISP.MOSI, RK4.1, U$1.SI (MOSI), X3.4
unnamed: 32U4.6 (UCAP), C13.2
unnamed: CON2.P$1 (V+), HX1.2 (D)
unnamed: BKLD.A, R2.2
unnamed: 20K.2, BJ1.3 (C), C7.1, CU2.1, U1.3 (AVDD), WGT.5
unnamed: LDPW12.A, R12.1
unnamed: Q6.1 (G), R5.2, RK12.2
unnamed: R10.2, RT2.2, U$2.1 (DQ)
unnamed: Q5.1 (G), R6.2, RK13.2
unnamed: C35.2, IC4.24 (CP2)
unnamed: OUT.2, Q5.2 (D)
unnamed: R4.1, RT1.1, X1.1
unnamed: A+.C, A-.A, RK9.2
unnamed: IN.2, Q6.2 (D)
unnamed: RK15.2, TX.A
unnamed: B+.C, B-.A, RK11.2
unnamed: C9.2, RL1.1, U1.7 (INA-)
unnamed: R9.2, RT1.2, X1.2
unnamed: LDSLAVE.A, RK18.2
unnamed: RK3.2, U$1.SCK
unnamed: RK16.2, RXLD.A
unnamed: LDMEM.A, RK19.2
unnamed: LDPID.A, RK14.1
unnamed: LDIN.A, RK12.1
unnamed: LDOUT.A, RK13.1
unnamed: C35.1, IC4.23 (CP1)
unnamed: C34.2, IC4.22 (VCP)
unnamed: LDPW3.A, R14.2
unnamed: C29.1, IC4.20 (VGD)
unnamed: C31.1, IC4.1 (ISENA), R38.2
unnamed: BJ1.1 (B), U1.2 (BASE)
unnamed: 8.2K.2, 20K.1, U1.4 (VFB)
unnamed: C30.1, IC4.14 (ISENB), R26.2
unnamed: RK5.1, SJ3.1, U1.15 (RATE)
unnamed: 32U4.17 (XTAL1), CX1.2, RXT.2, X2.P$2
unnamed: C9.1, RL2.1, U1.8 (INA+)
unnamed: C28.1, IC4.5 (DECAY), R30.1, R37.2
unnamed: C25.1, IC4.6 (RCA), R25.2
unnamed: C26.1, IC4.9 (RCB), R27.2
unnamed: IC4.27 (SLEEP), R34.1
unnamed: IC4.17 (RESET), R33.1
unnamed: C27.1, IC4.8 (VREF), R28.2, R29.1
unnamed: IC4.26 (ENABLE), R35.2
unnamed: IC4.12 (USM1), R31.1, SJ7.2
unnamed: IC4.13 (USM0), R32.1, SJ8.2
unnamed: IC4.16 (SR), R36.2
RESET: 32U4.13 (/RESET), C11.1, CON_ISP.RESET, RK6.1, SJ1.2
RX: 32U4.20 (PD2(INT2/RXD1)), U$3.P$6
RXLED: 32U4.8 (PB0(SS)), RXLD.C
SCK: 32U4.9 (PB1(SCK)), CON_ISP.SCK, RK3.1, X3.3
SCL: 32U4.18 (PD0(INT0/OC0B/SCL)), J1.SCL (2), J2.SCL (2), RK2.2
SDA: 32U4.19 (PD1(INT1/SDA)), J1.SDA (3), J2.SDA (3), RK1.2
TX: 32U4.21 (PD3(INT3/TXD1)), U$3.P$7
TXLED: 32U4.22 (PD5(XCK/CTS)), TX.C
USBC_N: RUSB1.2, X4.2
USBC_P: RUSB2.2, X4.3
USB_N: 32U4.3 (D-), RUSB1.1
USB_P: 32U4.4 (D+), RUSB2.1
VDD: C1.1, CU3.1, CU7.1, D1.C, D2.C, D4.C, IC1.1 (VI), R12.2, X3.1, X3.2
VUSB: 32U4.7 (VBUS), CU9.2, D4.A, X4.1
XTAL1: 32U4.16 (XTAL2), CX2.2, RXT.1, X2.P$1

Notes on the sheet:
Flash Memory
USB
Power Supply
LoRa RN2483
PID
One wire
I2C
5V_protect
POWER_LEDS
COM_LEDS
3.3V LDO
STEPPER
VCC: 2.7-5.5V
VBG = 1.25V
AVDD = VBG(R1+R2)/R1
Default: Closed - Data rate set to 10SPS
Open jumper to set to 80SPS Increases noise per read
Red
Black
White
IO: 2.7-5.5V
Shield
Yellow
ATMega32u4
Load cell 24bits ADC
SPI Slave
GND
+5V
SPI
FOOD
(pull up on COM Led)
S2_DIR
S2_STEP

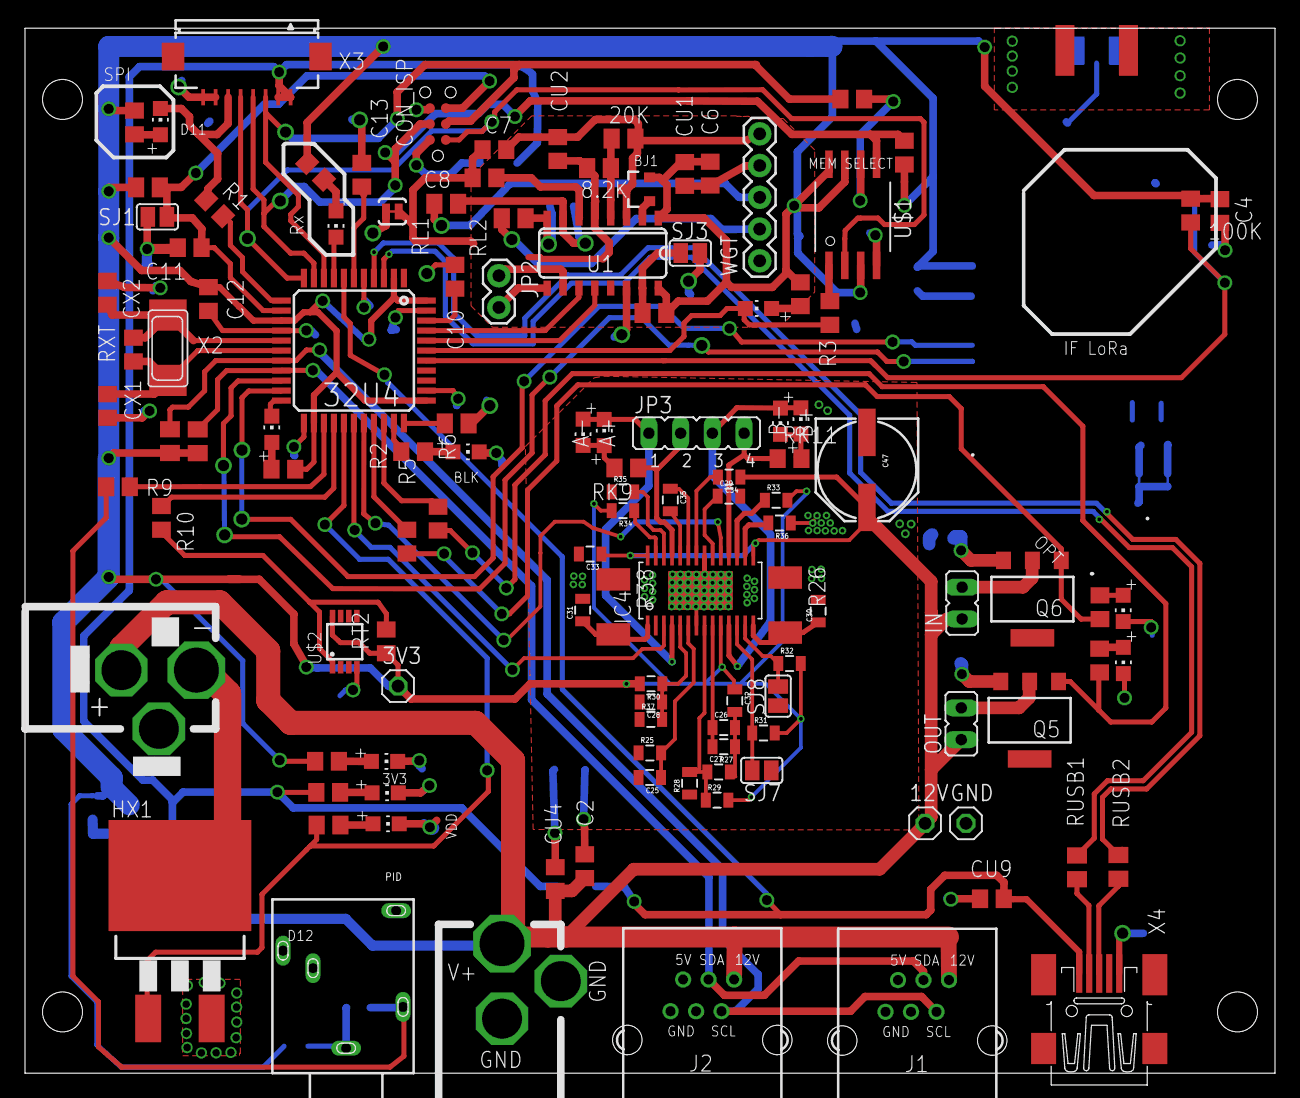
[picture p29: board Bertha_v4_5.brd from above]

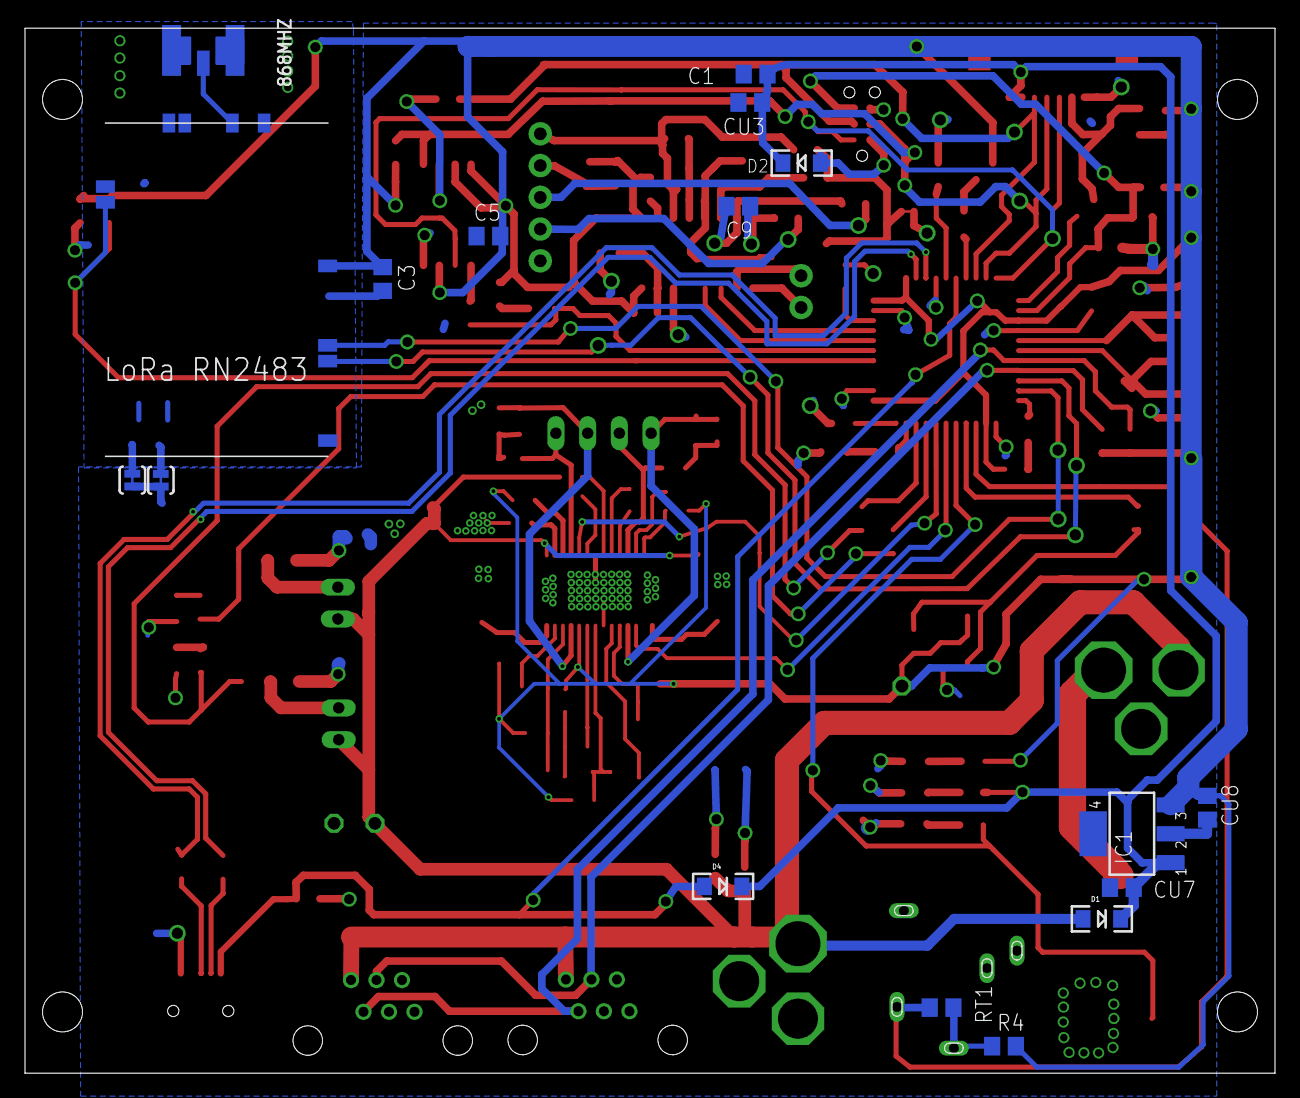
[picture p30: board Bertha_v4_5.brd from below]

Board: 4 copper layers, 100.0 x 83.6 mm, 137 parts (17 on the bottom side), 96 nets.

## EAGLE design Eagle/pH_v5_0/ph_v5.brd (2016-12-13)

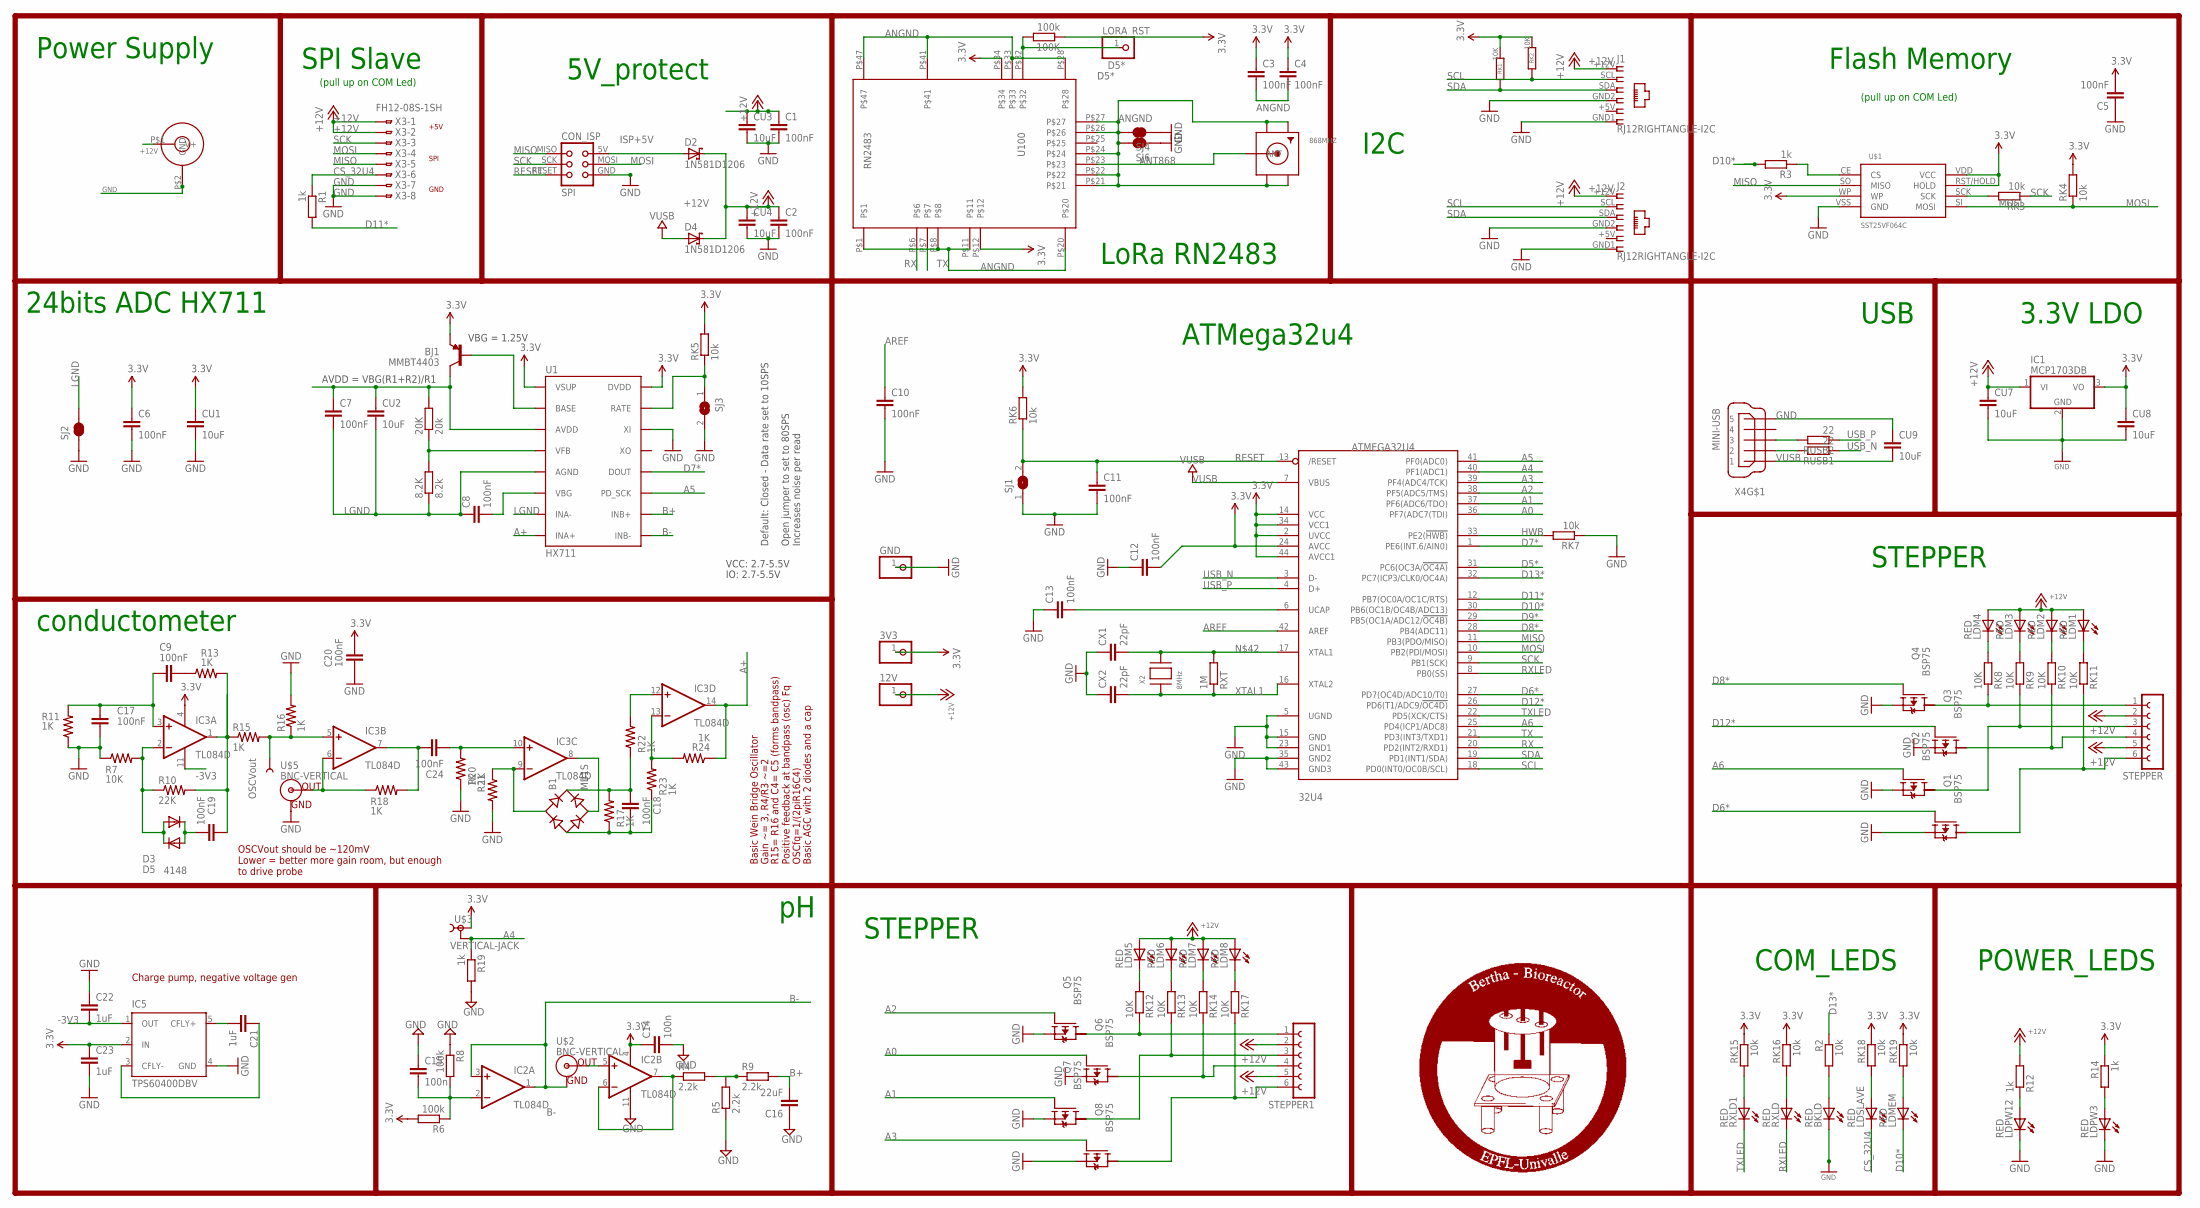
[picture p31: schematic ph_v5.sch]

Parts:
3V3, 12V: PINHD-1X1; 1X01
8.2K: 8.2k; M0805
20K: 20k; M0805
32U4: ATMEGA32U4; TQFP44
100K: 100k; R0805
868MHZ: SMACONNECTOR_EDGE; SMA_EDGELAUNCH
B1: MB1S; SOIC-4
BJ1: MMBT4403; SOT23-3
BKLD: RED; CHIP-LED0805
C1, C2, C3, C4, C5, C6, C7, C8, C10, C11, C12, C13: 100nF; C1206
C9, C17, C18, C19, C20, C24: 100nF; 1206
C14, C15: 100n; C1206
C16: 22uF; C1206
C21, C22, C23: 1uF; 1206
CON1: JACK_DC_BARREL; DC_BARREL
CON_ISP: SPI; TC2030-MCP-NL
CU1, CU2, CU3, CU4, CU7, CU8, CU9: 10uF; C1206
CX1, CX2: 22pF; C1206
D2, D4: 1N581D1206; LED-1206
D3, D5: 4148; SOD123
GND: PINHD-1X1; 1X01
IC1: MCP1703DB; SOT223
IC2, IC3: TL084D; SO14
IC5: TPS60400DBV; SOT23-DBV
J1, J2: RJ12RIGHTANGLE-I2C; RJ12-RIGHTANGLE-I2C
LDM1, LDM2, LDM3, LDM4, LDM5, LDM6, LDM7, LDM8: RED; CHIP-LED0805
LDMEM: RED; CHIP-LED0805
LDPW3, LDPW12: RED; CHIP-LED0805
LDSLAVE: RED; CHIP-LED0805
LORA_RST: PINHD-1X1; 1X01
Q1, Q2, Q3, Q4, Q5, Q6, Q7, Q8: BSP75; PG-SOT-223
R1, R3, R12, R14, R19: 1k; R0805
R2: 10k; R0805
R4, R5, R9: 2.2k; R0805
R6, R8: 100k; R0805
R7: 10K; 0805
R10: 22K; 0805
R11, R13, R15, R16, R17, R18, R20, R21, R22, R23, R24: 1K; 0805
RK1, RK2: 10K; M0805
RK3, RK4, RK15, RK16, RK18, RK19: 10k; R0805
RK5, RK6, RK7: 10k; M0805
RK8, RK9, RK10, RK11, RK12, RK13, RK14, RK17: 10K; R0805
RUSB1, RUSB2: 22; M1206
RXLD, RXLD1: RED; CHIP-LED0805
RXT: 1M; R0805
SJ1, SJ3: SJ
SJ2, SJ4, SJ6: JUMPER-PAD-2-NC_BY_TRACE; PAD-JUMPER-2-NC_BY_TRACE_YES_SILK
STEPPER, STEPPER1: FE06-1; FE06
TP5: OSCVout; PAD.03X.03
U1: HX711; SO16
U100: RN2483
U$1: SST25VF064C; SOIC_8-LEAD
U$2, U$5: BNC-VERTICAL
U$3: VERTICAL-JACK
X2: 8MHz; NX6035
X3: FH12-08S-1SH
X4: MINI-USB; 32005-201

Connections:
3.3V: 3V3.1, 32U4.2 (UVCC), 32U4.14 (VCC), 32U4.24 (AVCC), 32U4.34 (VCC1), 32U4.44 (AVCC1), 100K.1, BJ1.2 (E), C3.1, C4.1, C5.2, C6.1, C12.2, C14.1, C20.1, C23.1, CU1.1, CU8.1, IC1.3 (VO), IC2.4 (V+), IC3.4 (V+), IC5.2 (IN), R6.2, R14.1, RK1.1, RK2.1, RK4.2, RK5.2, RK6.2, RK15.1, RK16.1, RK18.1, RK19.1, U1.1 (VSUP), U1.16 (DVDD), U100.P$12, U100.P$34, U$1.RST/HOLD (HOLD), U$1.VDD (VCC), U$1.WP, U$3.P$1 (1)
+12V: 12V.1, C1.1, C2.1, CON1.P$1 (V+), CU3.1, CU4.1, CU7.1, D2.C, D4.C, IC1.1 (VI), J1.+12V (1), J2.+12V (1), LDM1.A, LDM2.A, LDM3.A, LDM4.A, LDM5.A, LDM6.A, LDM7.A, LDM8.A, R12.2, STEPPER.2, STEPPER.5, STEPPER1.2, STEPPER1.5, X3.1, X3.2
-3V3: C22.2, IC3.11 (V-), IC5.1 (OUT)
A0: 32U4.36 (PF7(ADC7(TDI)), Q6.1 (G)
A1: 32U4.37 (PF6(ADC6/TDO)), Q7.1 (G)
A2: 32U4.38 (PF5(ADC5/TMS)), Q5.1 (G)
A3: 32U4.39 (PF4(ADC4/TCK)), Q8.1 (G)
A4: 32U4.40 (PF1(ADC1)), R19.1, U$3.P$2 (2)
A5: 32U4.41 (PF0(ADC0)), U1.11 (PD_SCK)
A6: 32U4.25 (PD4(ICP1/ADC8)), Q2.1 (G)
A+: IC3.14 (OUT), R24.1, U1.8 (INA+)
ANGND: 868MHZ.GND@1 (GND4), 868MHZ.GND@2 (GND3), 868MHZ.GND@3 (GND2), 868MHZ.GND@4 (GND1), C3.2, C4.2, SJ4.2, SJ6.2, U100.P$1, U100.P$8, U100.P$11, U100.P$20, U100.P$21, U100.P$22, U100.P$24, U100.P$26, U100.P$27, U100.P$28, U100.P$33, U100.P$41, U100.P$47
ANT868: 868MHZ.P (ANT), U100.P$23
AREF: 32U4.42 (AREF), C10.1
B+: C16.2, R9.2, U1.10 (INB+)
B-: IC2.1 (OUT), IC2.3 (+IN), U1.9 (INB-), U$2.G (GND)
CN3: C8.2, U1.6 (VBG)
CS_32U4: LDSLAVE.C, R1.1, X3.6
D5*: 32U4.31 (PC6(OC3A/!OC4A)), 100K.2, LORA_RST.1, U100.P$32
D6*: 32U4.27 (PD7(OC4D/ADC10/T0)), Q1.1 (G)
D7*: 32U4.1 (PE6(INT.6/AIN0)), U1.12 (DOUT)
D8*: 32U4.28 (PB4(ADC11)), Q4.1 (G)
D9*: 32U4.29 (PB5(OC1A/ADC12/!OC4B))
D10*: 32U4.30 (PB6(OC1B/OC4B/ADC13)), LDMEM.C, R3.2
D11*: 32U4.12 (PB7(OC0A/OC1C/RTS)), R1.2
D12*: 32U4.26 (PD6(T1/ADC9/!OC4D)), Q3.1 (G)
D13*: 32U4.32 (PC7(ICP3/CLK0/OC4A)), R2.1
GND: 32U4.5 (UGND), 32U4.15 (GND), 32U4.23 (GND1), 32U4.35 (GND2), 32U4.43 (GND3), BKLD.C, C1.2, C2.2, C5.1, C6.2, C10.2, C11.2, C12.1, C13.1, C14.2, C15.1, C16.1, C17.1, C20.2, C22.1, C23.2, CON1.P$2 (GND), CON_ISP.GND, CU1.2, CU3.2, CU4.2, CU7.2, CU8.2, CU9.1, CX1.1, CX2.1, GND.1, IC1.2 (GND), IC2.11 (V-), IC5.4 (GND), J1.GND1 (6), J1.GND2 (4), J2.GND1 (6), J2.GND2 (4), LDPW3.C, LDPW12.C, Q1.3 (S), Q2.3 (S), Q3.3 (S), Q4.3 (S), Q5.3 (S), Q6.3 (S), Q7.3 (S), Q8.3 (S), R5.1, R7.1, R8.1, R11.1, R16.2, R19.2, R20.1, R21.2, RK7.1, SJ1.1, SJ2.1, SJ3.2, SJ4.1, SJ6.1, U1.14 (XI), U$1.VSS (GND), U$5.G (GND), X3.7, X3.8, X4.5
HWB: 32U4.33 (PE2(!HWB)), RK7.2
ISP+5V: CON_ISP.5V (VCC), D2.A
LGND: 8.2K.1, C7.2, C8.1, CU2.2, SJ2.2, U1.5 (AGND), U1.7 (INA-)
MISO: 32U4.11 (PB3(PDO/MISO)), CON_ISP.MISO, U$1.SO (MISO), X3.5
MOSI: 32U4.10 (PB2(PDI/MOSI)), CON_ISP.MOSI, RK4.1, U$1.SI (MOSI), X3.4
unnamed: 32U4.6 (UCAP), C13.2
unnamed: Q5.2 (D), RK12.1, STEPPER1.1
unnamed: BKLD.A, R2.2
unnamed: Q7.2 (D), RK13.1, STEPPER1.3
unnamed: 20K.2, BJ1.3 (C), C7.1, CU2.1, U1.3 (AVDD)
unnamed: Q6.2 (D), RK14.1, STEPPER1.4
unnamed: LDPW12.A, R12.1
unnamed: Q8.2 (D), RK17.1, STEPPER1.6
unnamed: LDM5.C, RK12.2
unnamed: R3.1, U$1.CE (CS)
unnamed: LDM6.C, RK13.2
unnamed: LDM7.C, RK14.2
unnamed: LDM8.C, RK17.2
unnamed: Q4.2 (D), RK8.1, STEPPER.1
unnamed: Q2.2 (D), RK9.1, STEPPER.3
unnamed: Q3.2 (D), RK10.1, STEPPER.4
unnamed: R4.2, R5.2, R9.1
unnamed: D3.A, D5.C, IC3.2 (-IN), R7.2, R10.1
unnamed: Q1.2 (D), RK11.1, STEPPER.6
unnamed: C9.1, R13.1
unnamed: IC2.5 (+IN), U$2.S (OUT)
unnamed: LDSLAVE.A, RK18.2
unnamed: RK3.2, U$1.SCK
unnamed: RK16.2, RXLD.A
unnamed: LDMEM.A, RK19.2
unnamed: C19.1, IC3.1 (OUT), R10.2, R13.2, R15.1
unnamed: C15.2, IC2.2 (-IN), R6.1, R8.2
unnamed: IC2.6 (-IN), IC2.7 (OUT), R4.1
unnamed: IC3.5 (+IN), R15.2, R16.1, TP5.P$1
unnamed: C9.2, C17.2, IC3.3 (+IN), R11.2
unnamed: LDM4.C, RK8.2
unnamed: LDM3.C, RK9.2
unnamed: LDM2.C, RK10.2
unnamed: LDPW3.A, R14.2
unnamed: IC3.6 (-IN), R18.1, U$5.S (OUT)
unnamed: C24.1, IC3.7 (OUT), R18.2
unnamed: LDM1.C, RK11.2
unnamed: BJ1.1 (B), U1.2 (BASE)
unnamed: 8.2K.2, 20K.1, U1.4 (VFB)
unnamed: C24.2, IC3.10 (+IN), R20.2
unnamed: RK5.1, SJ3.1, U1.15 (RATE)
unnamed: 32U4.17 (XTAL1), CX1.2, RXT.2, X2.P$2
unnamed: B1.~2 (AC2), IC3.8 (OUT)
unnamed: C19.2, D3.C, D5.A
unnamed: C21.1, IC5.3 (CFLY-)
unnamed: C21.2, IC5.5 (CFLY+)
unnamed: B1.-, C18.1, R17.1, R23.1
unnamed: B1.~1 (AC1), IC3.9 (-IN), R21.1
unnamed: B1.+, C18.2, R17.2, R22.1
unnamed: IC3.12 (+IN), R22.2
unnamed: IC3.13 (-IN), R23.2, R24.2
unnamed: RK15.2, RXLD1.A
RESET: 32U4.13 (/RESET), C11.1, CON_ISP.RESET, RK6.1, SJ1.2
RX: 32U4.20 (PD2(INT2/RXD1)), U100.P$6
RXLED: 32U4.8 (PB0(SS)), RXLD.C
SCK: 32U4.9 (PB1(SCK)), CON_ISP.SCK, RK3.1, X3.3
SCL: 32U4.18 (PD0(INT0/OC0B/SCL)), J1.SCL (2), J2.SCL (2), RK2.2
SDA: 32U4.19 (PD1(INT1/SDA)), J1.SDA (3), J2.SDA (3), RK1.2
TX: 32U4.21 (PD3(INT3/TXD1)), U100.P$7
TXLED: 32U4.22 (PD5(XCK/CTS)), RXLD1.C
USBC_N: RUSB1.2, X4.2
USBC_P: RUSB2.2, X4.3
USB_N: 32U4.3 (D-), RUSB1.1
USB_P: 32U4.4 (D+), RUSB2.1
VUSB: 32U4.7 (VBUS), CU9.2, D4.A, X4.1
XTAL1: 32U4.16 (XTAL2), CX2.2, RXT.1, X2.P$1

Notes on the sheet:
Flash Memory
USB
Power Supply
LoRa RN2483
I2C
5V_protect
POWER_LEDS
COM_LEDS
3.3V LDO
STEPPER
VCC: 2.7-5.5V
VBG = 1.25V
AVDD = VBG(R1+R2)/R1
Default: Closed - Data rate set to 10SPS
Open jumper to set to 80SPS Increases noise per read
IO: 2.7-5.5V
ATMega32u4
24bits ADC HX711
SPI Slave
GND
+5V
SPI
(pull up on COM Led)
Basic Wein Bridge Oscillator
Gain ~= 3, R4/R3 ~=2
R15= R16 and C4= C5 (forms bandpass) Positive feedback at bandpass (osc) Fq
OSCfq=1/(2piR16C4)
Basic AGC with 2 diodes and a cap
OSCVout should be ~120mV Lower = better more gain room, but enough to drive probe
conductometer
Charge pump, negative voltage gen

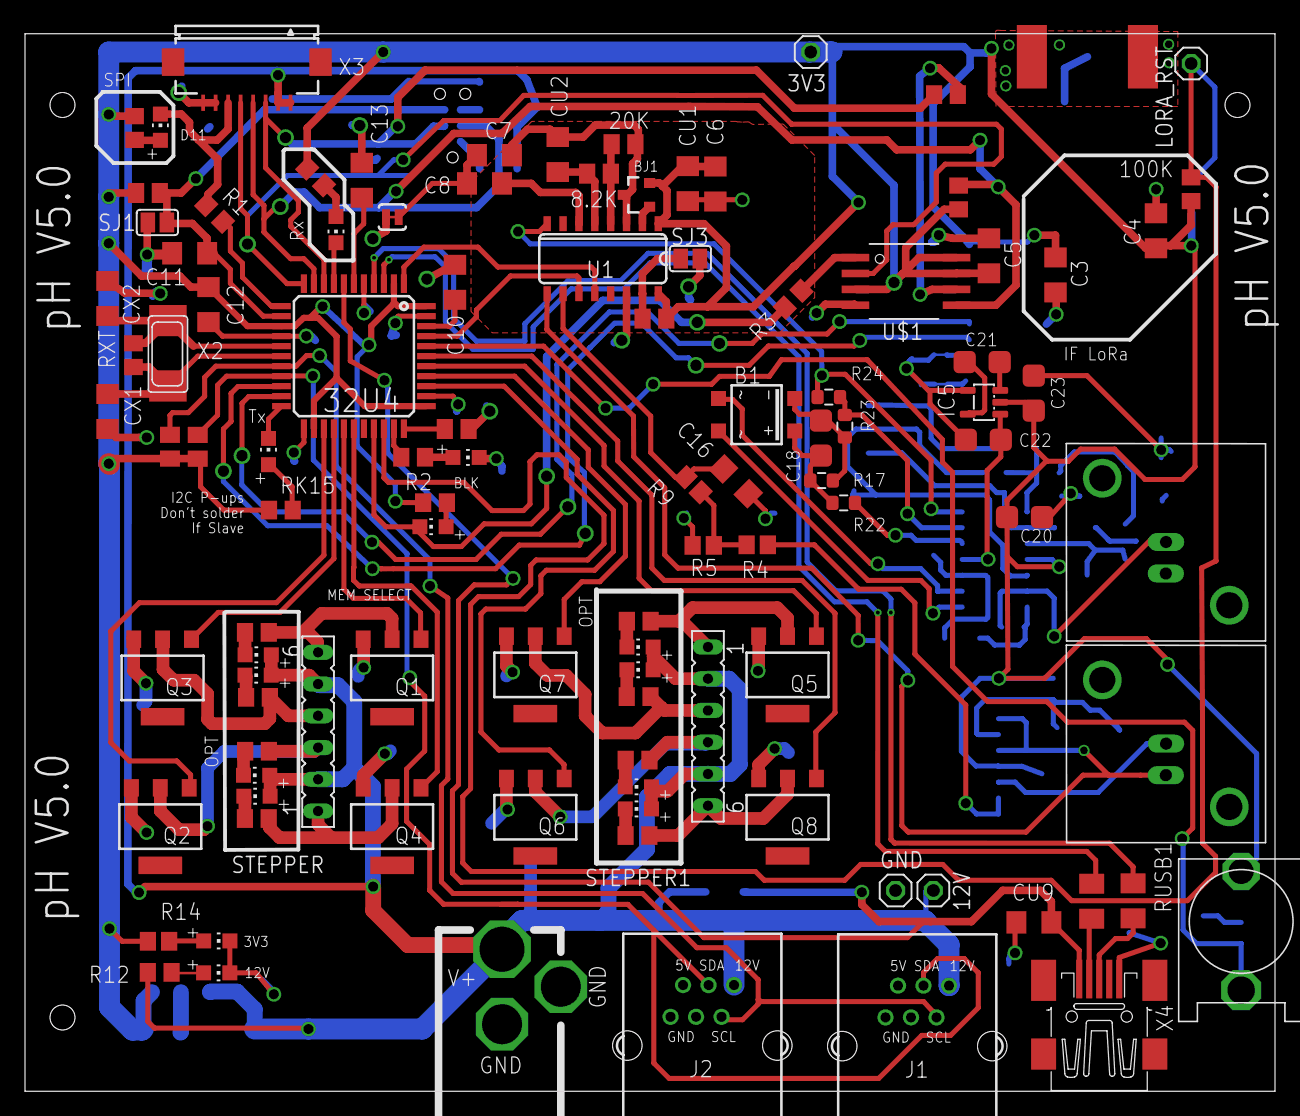
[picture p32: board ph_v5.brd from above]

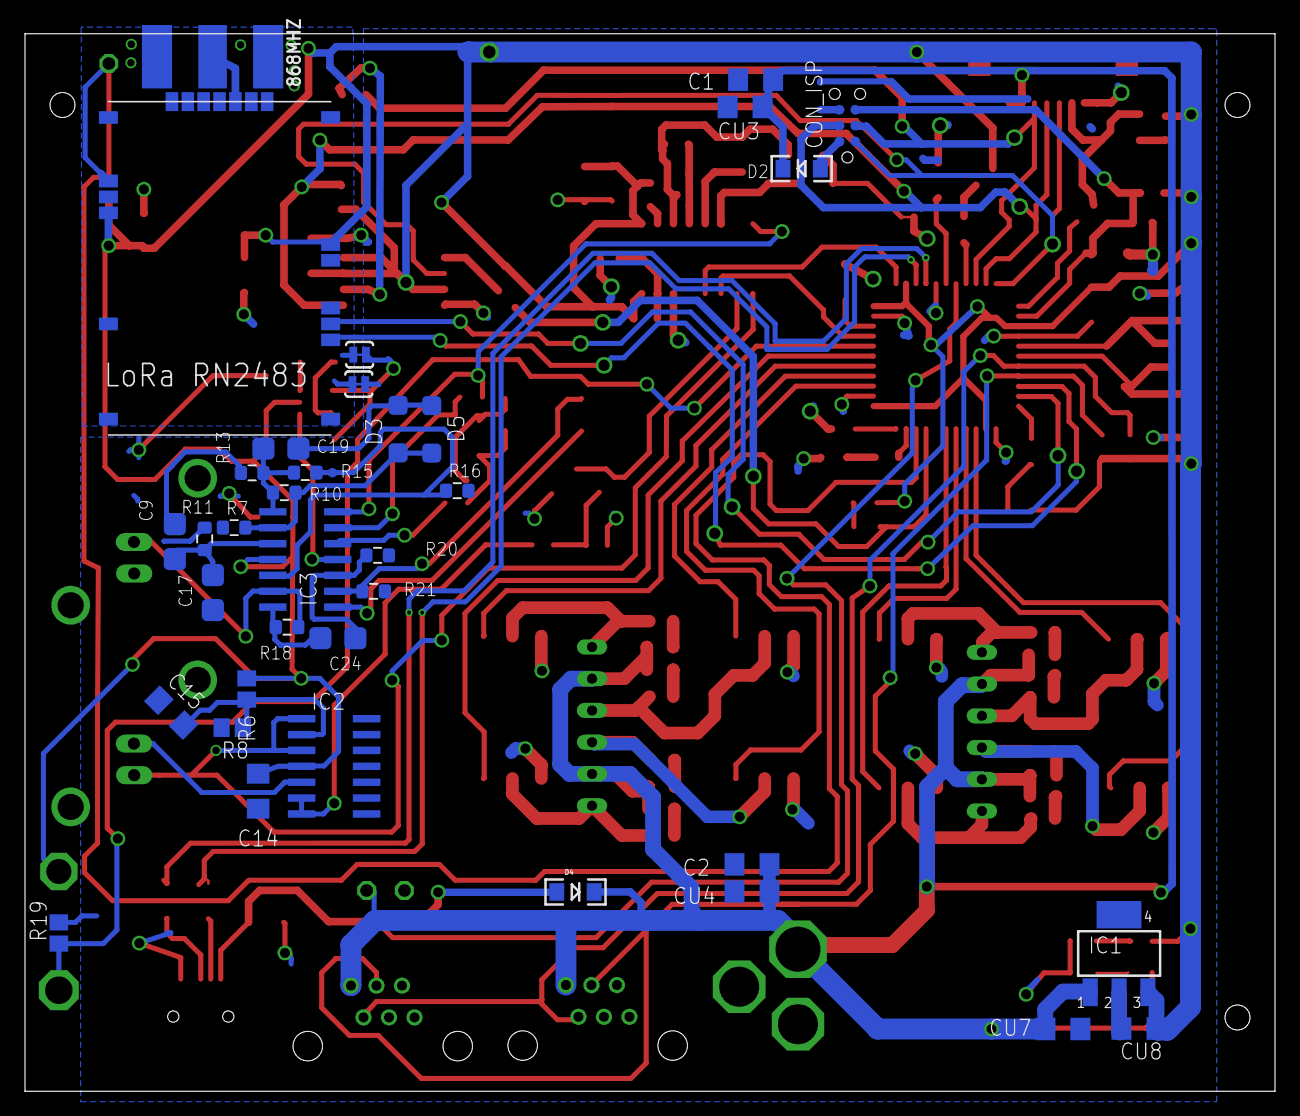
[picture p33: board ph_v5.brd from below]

Board: 4 copper layers, 100.0 x 84.6 mm, 142 parts (37 on the bottom side), 98 nets.

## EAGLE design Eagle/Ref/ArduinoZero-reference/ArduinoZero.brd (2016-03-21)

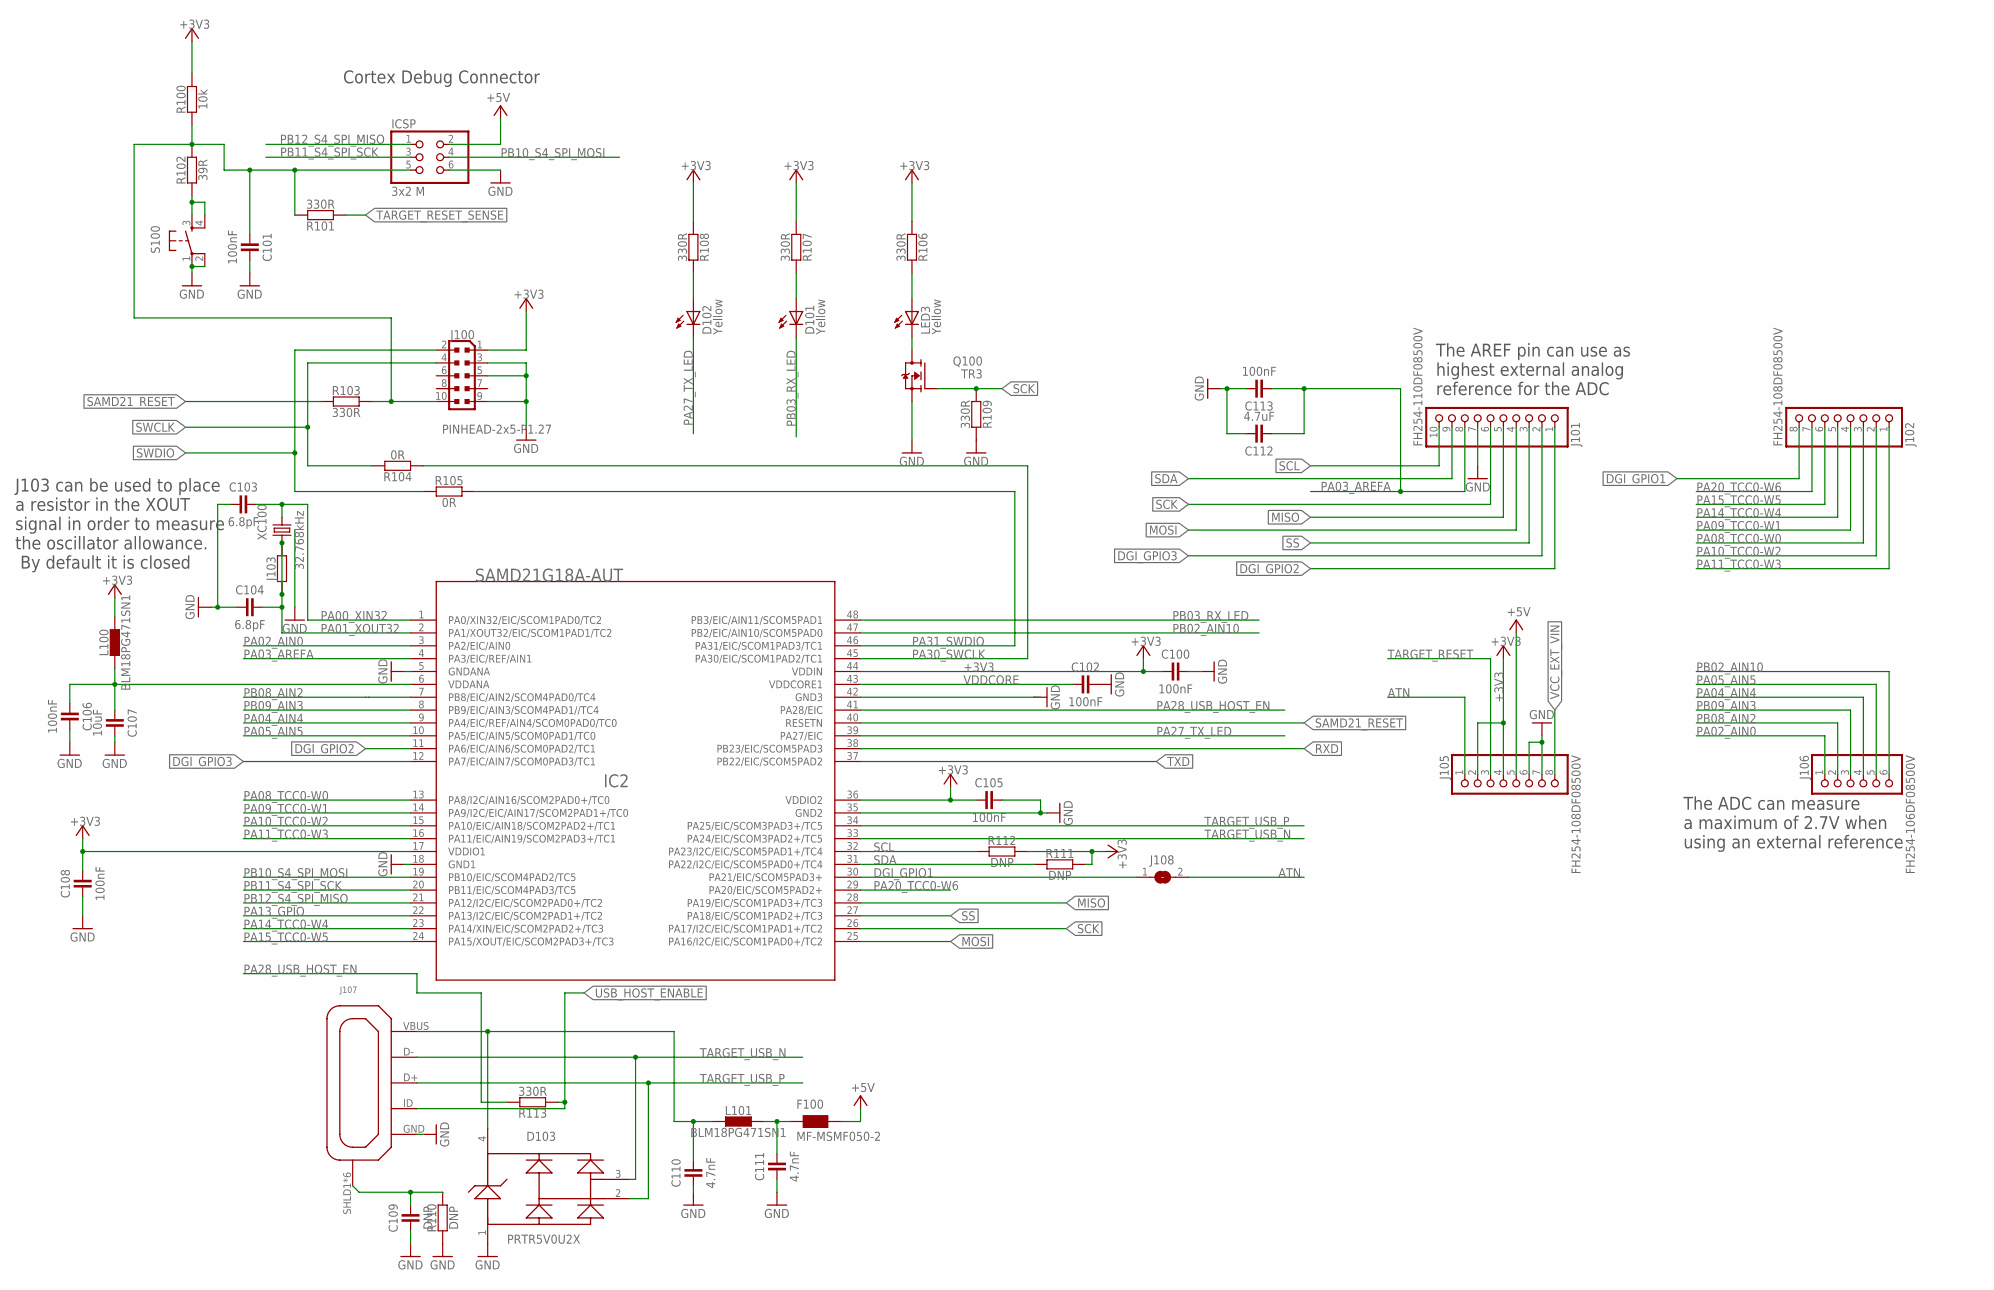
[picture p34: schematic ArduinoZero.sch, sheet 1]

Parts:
C100, C101, C102, C105, C106, C108, C113: 100nF; C0402
C103, C104: 6.8pF; C0402
C107: 10uF; C0603
C109: DNP; C0402
C110, C111: 4.7nF; C0402
C112: 4.7uF; C0603
D101, D102: Yellow; CHIPLED_0805
D103: PRTR5V0U2XB; SOT143B
F100: MF-MSMF050-2; WUERTH-ELEKTRONIK_1812
IC2: SAMD21G18A-AUT; TQFP48
ICSP: 3x2 M; 2X03
J100: PINHEAD-2x5-P1.27; PINHEAD_2X05_127
J101: FH254-110DF08500V; 1X10
J102, J105: FH254-108DF08500V; 1X08
J103: RESISTORS-0402; C0402
J106: FH254-106DF08500V; 1X06
J107: ZX62-AB-5PA; USB-MICRO-10103594
J108: SJ
L100, L101: BLM18PG471SN1; C0603
LED3: Yellow; CHIPLED_0805
R100: 10k; C0402
R101, R103, R106, R107, R108, R109, R113: 330R; C0402
R102: 39R; C0402
R104, R105: 0R; C0402
R110, R111, R112: DNP; C0402
S100: PUSHBUTTON3; TS42_4PINS
TR3: Q100; SOT-23
XC100: 32.768kHz; CRYSTAL_TC26SMD

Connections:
+3V3: C100.1, C105.1, C108.2, IC2.17 (VDDIO1), IC2.36 (VDDIO2), IC2.44 (VDDIN), J100.1, J105.2, J105.4, L100.2, R100.2, R106.1, R107.1, R108.1, R111.2, R112.2; also elsewhere on the board
+5V: F100.2, ICSP.2, J105.5; also elsewhere on the board
ATN: J105.1, J108.2
DGI_GPIO1: IC2.30 (PA21/EIC/SCOM5PAD3+), J102.8, J108.1; also elsewhere on the board
DGI_GPIO2: IC2.11 (PA6/EIC/AIN6/SCOM0PAD2/TC1), J101.1; also elsewhere on the board
DGI_GPIO3: IC2.12 (PA7/EIC/AIN7/SCOM0PAD3/TC1), J101.2; also elsewhere on the board
GND: C100.2, C101.2, C102.2, C103.1, C104.1, C105.2, C106.2, C107.2, C108.1, C109.1, C110.1, C111.1, C112.2, C113.2, D103.1, IC2.5 (GNDANA), IC2.18 (GND1), IC2.35 (GND2), IC2.42 (GND3), ICSP.6, J100.3, J100.5, J100.9, J101.7, J105.6, J105.7, J107.GND, R109.2, R110.1, S100.1, S100.2, TR3.2 (S), XC100.P$1 (GND); also elsewhere on the board
MISO: IC2.28 (PA19/EIC/SCOM1PAD3+/TC3), J101.5; also elsewhere on the board
MOSI: IC2.25 (PA16/I2C/EIC/SCOM1PAD0+/TC2), J101.4; also elsewhere on the board
unnamed: LED3.C, TR3.1 (D)
unnamed: R102.1, S100.3, S100.4
unnamed: C110.2, D103.4, J107.VBUS (VUSB), L101.1
unnamed: C106.1, C107.1, IC2.6 (VDDANA), L100.1
unnamed: C109.2, J107.SHLD1 (SH), J107.SHLD2 (SH), J107.SHLD3 (SH), J107.SHLD4 (SH), J107.SHLD5 (SH), J107.SHLD6 (SH), R110.2
unnamed: C111.2, F100.1, L101.2
unnamed: D102.A, R108.2
unnamed: D101.A, R107.2
unnamed: LED3.A, R106.2
PA00_XIN32: C103.2, IC2.1 (PA0/XIN32/EIC/SCOM1PAD0/TC2), XC100.2
PA01_XOUT32: C104.2, IC2.2 (PA1/XOUT32/EIC/SCOM1PAD1/TC2), J103.1, J103.2, XC100.1
PA02_AIN0: IC2.3 (PA2/EIC/AIN0), J106.1
PA03_AREFA: C112.1, C113.1, IC2.4 (PA3/EIC/REF/AIN1), J101.8
PA04_AIN4: IC2.9 (PA4/EIC/REF/AIN4/SCOM0PAD0/TC0), J106.4
PA05_AIN5: IC2.10 (PA5/EIC/AIN5/SCOM0PAD1/TC0), J106.5
PA08_TCC0-W0: IC2.13 (PA8/I2C/AIN16/SCOM2PAD0+/TC0), J102.3
PA09_TCC0-W1: IC2.14 (PA9/I2C/EIC/AIN17/SCOM2PAD1+/TC0), J102.4
PA10_TCC0-W2: IC2.15 (PA10/EIC/AIN18/SCOM2PAD2+/TC1), J102.2
PA11_TCC0-W3: IC2.16 (PA11/EIC/AIN19/SCOM2PAD3+/TC1), J102.1
PA13_GPIO: IC2.22 (PA13/I2C/EIC/SCOM2PAD1+/TC2)
PA14_TCC0-W4: IC2.23 (PA14/XIN/EIC/SCOM2PAD2+/TC3), J102.5
PA15_TCC0-W5: IC2.24 (PA15/XOUT/EIC/SCOM2PAD3+/TC3), J102.6
PA20_TCC0-W6: IC2.29 (PA20/EIC/SCOM5PAD2+), J102.7
PA27_TX_LED: D102.C, IC2.39 (PA27/EIC)
PA28_USB_HOST_EN: IC2.41 (PA28/EIC), R113.2
PA30_SWCLK: IC2.45 (PA30/EIC/SCOM1PAD2/TC1), R104.1
PA31_SWDIO: IC2.46 (PA31/EIC/SCOM1PAD3/TC1), R105.2
PB02_AIN10: IC2.47 (PB2/EIC/AIN10/SCOM5PAD0), J106.6
PB03_RX_LED: D101.C, IC2.48 (PB3/EIC/AIN11/SCOM5PAD1)
PB08_AIN2: IC2.7 (PB8/EIC/AIN2/SCOM4PAD0/TC4), J106.2
PB09_AIN3: IC2.8 (PB9/EIC/AIN3/SCOM4PAD1//TC4), J106.3
PB10_S4_SPI_MOSI: IC2.19 (PB10/EIC/SCOM4PAD2/TC5), ICSP.4
PB11_S4_SPI_SCK: IC2.20 (PB11/EIC/SCOM4PAD3/TC5), ICSP.3
PB12_S4_SPI_MISO: IC2.21 (PA12/I2C/EIC/SCOM2PAD0+/TC2), ICSP.1
RXD: IC2.38 (PB23/EIC/SCOM5PAD3); also elsewhere on the board
SAMD21_RESET: IC2.40 (RESETN), R103.1; also elsewhere on the board
SCK: IC2.26 (PA17/I2C/EIC/SCOM1PAD1+/TC2), J101.6, R109.1, TR3.3 (G); also elsewhere on the board
SCL: IC2.32 (PA23/I2C/EIC/SCOM5PAD1+/TC4), J101.10, R112.1; also elsewhere on the board
SDA: IC2.31 (PA22/I2C/EIC/SCOM5PAD0+/TC4), J101.9, R111.1; also elsewhere on the board
SS: IC2.27 (PA18/EIC/SCOM1PAD2+/TC3), J101.3; also elsewhere on the board
SWCLK: J100.4, R104.2; also elsewhere on the board
SWDIO: J100.2, R105.1; also elsewhere on the board
TARGET_RESET: C101.1, ICSP.5, J100.10, J105.3, R100.1, R101.2, R102.2, R103.2
TARGET_RESET_SENSE: R101.1; also elsewhere on the board
TARGET_USB_N: D103.3, IC2.33 (PA24/EIC/SCOM3PAD2+/TC5), J107.D-
TARGET_USB_P: D103.2, IC2.34 (PA25/EIC/SCOM3PAD3+/TC5), J107.D+
TXD: IC2.37 (PB22/EIC/SCOM5PAD2); also elsewhere on the board
USB_HOST_ENABLE: J107.ID, R113.1; also elsewhere on the board
VCC_EXT_VIN: J105.8; also elsewhere on the board
VDDCORE: C102.1, IC2.43 (VDDCORE1)

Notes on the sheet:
Cortex Debug Connector
J103 can be used to place a resistor in the XOUT signal in order to measure the oscillator allowance. By default it is closed
The ADC can measure a maximum of 2.7V when using an external reference
The AREF pin can use as highest external analog reference for the ADC

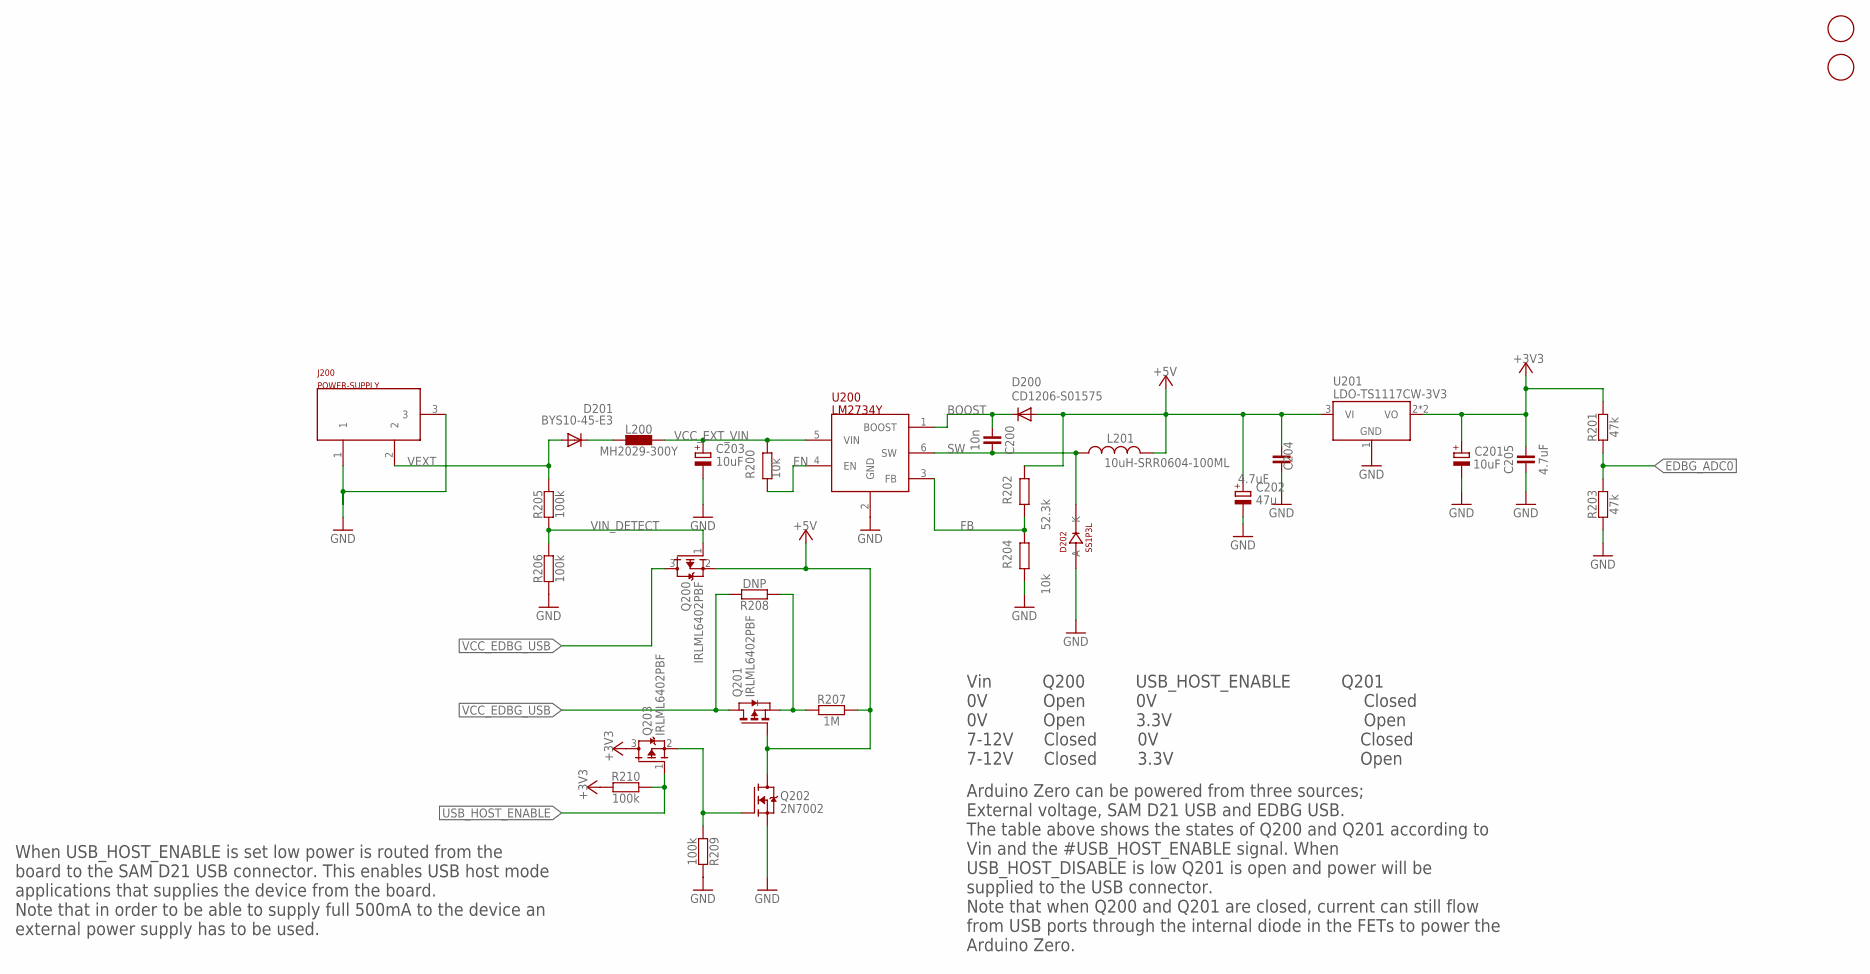
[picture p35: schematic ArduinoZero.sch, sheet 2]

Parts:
C200: 10n; C0402
C201, C203: 10uF; PANASONIC_D
C202: 47u; PANASONIC_D
C204, C205: 4.7uF; C0603
D200: CD1206-S01575; MINIMELF
D201: BYS10-45-E3; MINIMELF
D202: SS1P3L; DO220AAL
FD1, FD2: FIDUCIALMOUNT; FIDUCIA-MOUNT
J200: POWER-SUPPLY; POWERSUPPLY_DC-21MM
L200: MH2029-300Y; C0805
L201: 10uH-SRR0604-100ML; SRR0604
Q200, Q203: IRLML6402PBF; SOT323
Q201: IRLML6402PBF; SOT-23
Q202: 2N7002; SOT23
R200, R204: 10k; C0402
R201, R203: 47k; C0402
R202: 52.3k; C0402
R205, R206, R209, R210: 100k; C0402
R207: 1M; C0402
R208: DNP; C0402
U200: LM2734Y; SOT23-6
U201: LDO-TS1117CW-3V3; SOT223

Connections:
+3V3: C201.+, C205.2, Q203.3 (D), R201.2, R210.1, U201.2 (VO), U201.4 (VO); also elsewhere on the board
+5V: C202.+, C204.1, D200.A, L201.P$2 (2), Q200.2 (S), Q201.3 (G), Q202.3 (D), R202.1, R207.2, U201.3 (VI); also elsewhere on the board
BOOST: C200.1, D200.C, U200.1 (BOOST)
EDBG_ADC0: R201.1, R203.2; also elsewhere on the board
EN: R200.2, U200.4 (EN)
FB: R202.2, R204.1, U200.3 (FB)
GND: C201.-, C202.-, C203.-, C204.2, C205.1, D202.P$2 (A), J200.1, J200.3, Q202.2 (S), R203.1, R204.2, R206.1, R209.2, U200.2 (GND), U201.1 (GND); also elsewhere on the board
unnamed: Q201.2 (S), R207.1, R208.1
unnamed: D201.C, L200.1
unnamed: Q202.1 (G), Q203.2 (S), R209.1
SW: C200.2, D202.P$1 (K), L201.P$1 (1), U200.6 (SW)
USB_HOST_ENABLE: Q203.1 (G), R210.2; also elsewhere on the board
VCC_EDBG_USB: Q200.3 (D), Q201.1 (D), R208.2; also elsewhere on the board
VCC_EXT_VIN: C203.+, L200.2, R200.1, U200.5 (VIN); also elsewhere on the board
VEXT: D201.A, J200.2, R205.2
VIN_DETECT: Q200.1 (G), R205.1, R206.2

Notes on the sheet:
Arduino Zero can be powered from three sources; External voltage, SAM D21 USB and EDBG USB. The table above shows the states of Q200 and Q201 according to Vin and the #USB_HOST_ENABLE signal. When USB_HOST_DISABLE is low Q201 is open and power will be supplied to the USB connector. Note that when Q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
Vin Q200 USB_HOST_ENABLE Q201 0V Open 0V Closed 0V Open 3.3V Open 7-12V Closed 0V Closed 7-12V Closed 3.3V Open
When USB_HOST_ENABLE is set low power is routed from the board to the SAM D21 USB connector. This enables USB host mode applications that supplies the device from the board. Note that in order to be able to supply full 500mA to the device an external power supply has to be used.

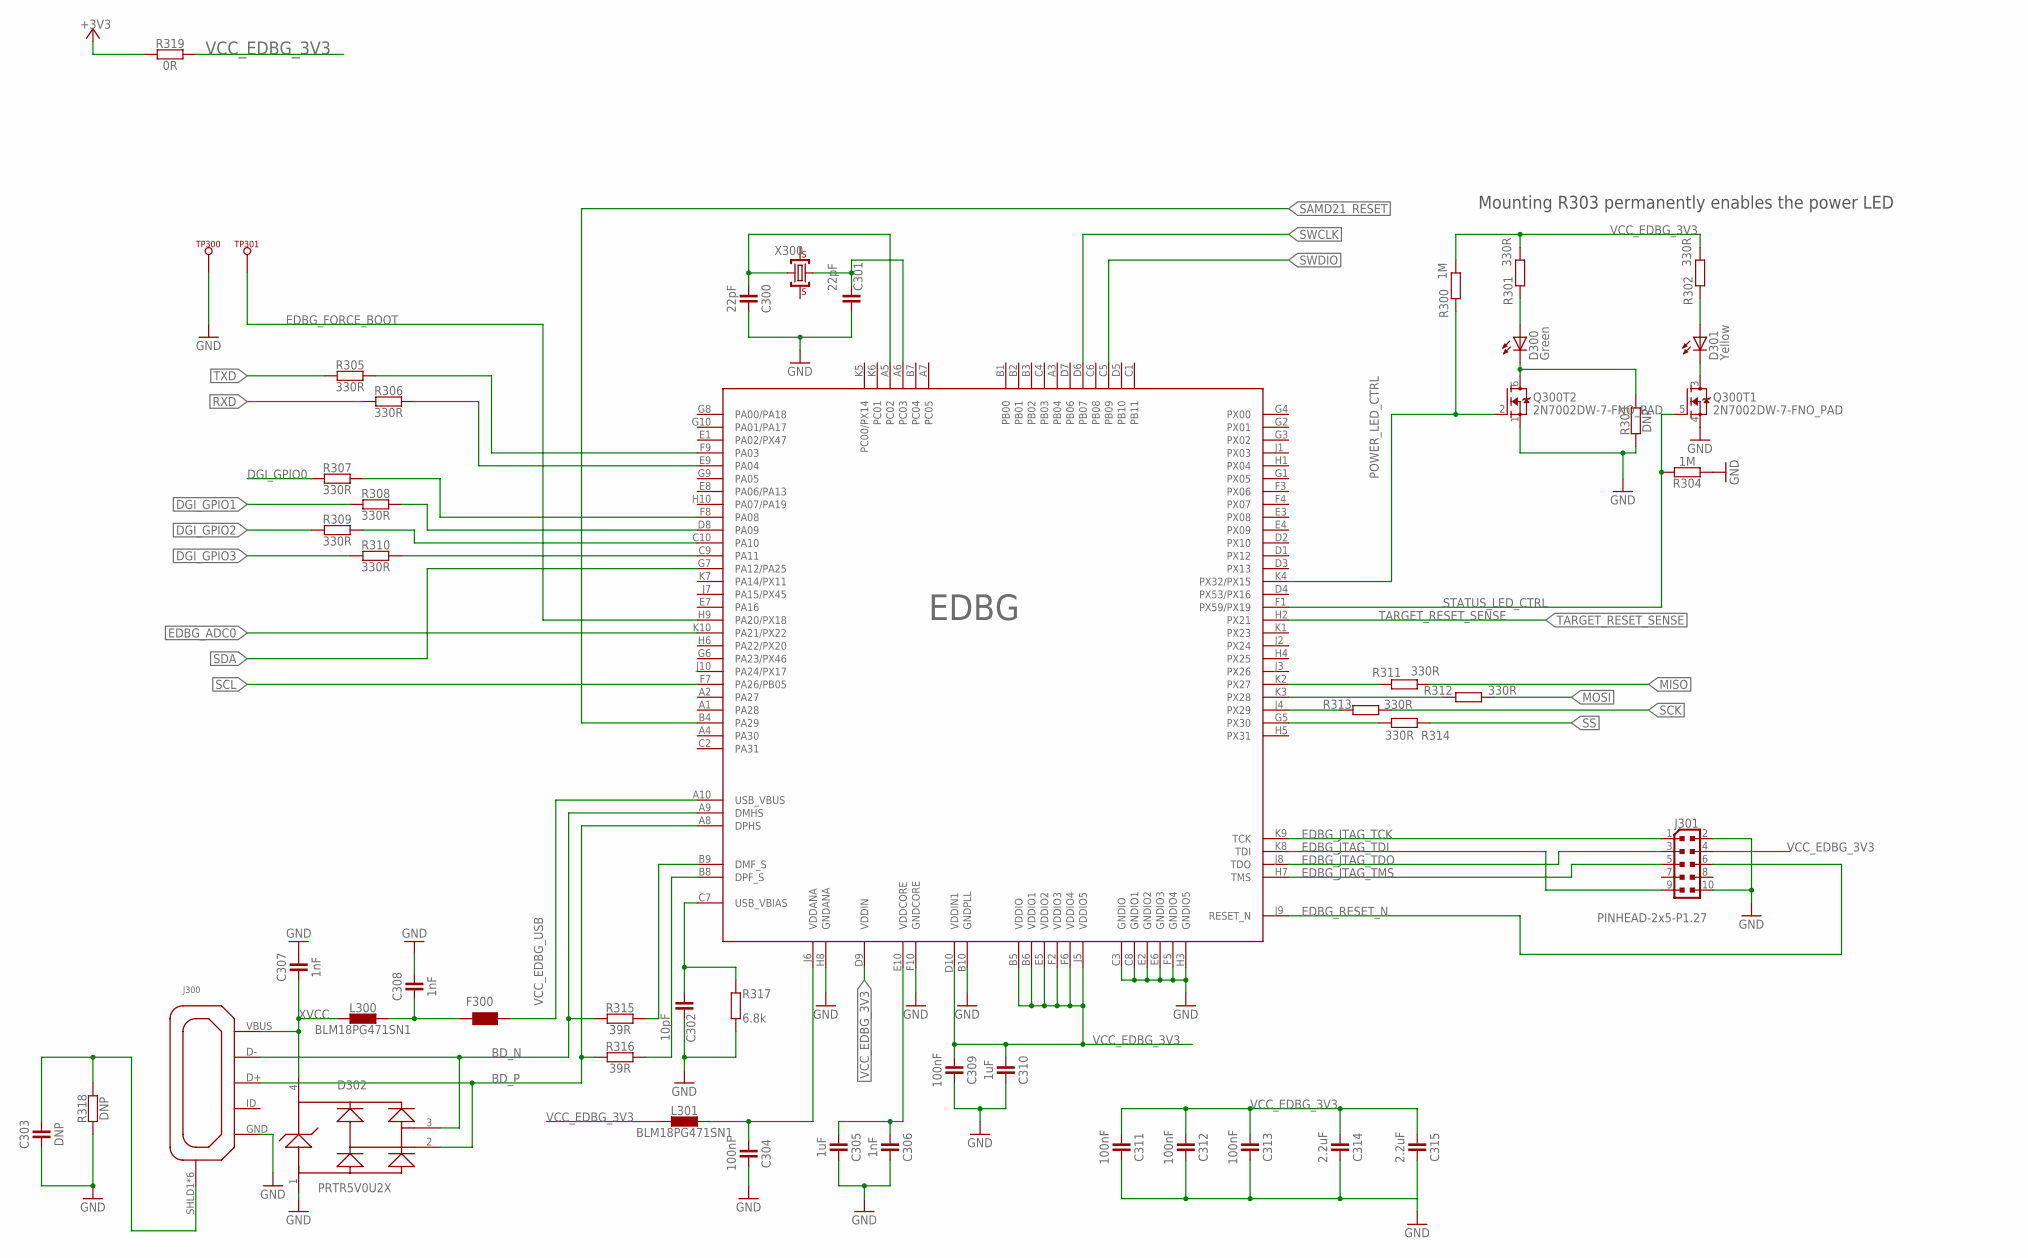
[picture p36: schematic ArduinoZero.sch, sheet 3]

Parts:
C300, C301: 22pF; C0402
C302: 10pF; C0402
C303: DNP; C0402
C304, C309, C311, C312, C313: 100nF; C0402
C305, C310: 1uF; C0402
C306, C307, C308: 1nF; C0402
C314, C315: 2.2uF; C0402
D300: Green; CHIPLED_0805
D301: Yellow; CHIPLED_0805
D302: PRTR5V0U2XB; SOT143B
EDBG: EDBG; VFBGA100
F300: WUERTH-ELEKTRONIK_WE-CBF_1812; WUERTH-ELEKTRONIK_1812
J300: ZX62-AB-5PA; USB-MICRO-10103594
J301: PINHEAD-2x5-P1.27; PINHEAD_2X05_127
L300, L301: BLM18PG471SN1; C0603
Q300: 2N7002DW-7-FNO_PAD; PWR_SC70-6L2
R300, R304: 1M; C0402
R301, R302, R305, R306, R307, R308, R309, R310, R311, R312, R313, R314: 330R; C0402
R303, R318: DNP; C0402
R315, R316: 39R; C0402
R317: 6.8k; C0402
R319: 0R; C0402
TP300, TP301: TP_SP; TP-SP
X300: 12mHz-12pF-K7; CRYSTAL-5.4-3.2

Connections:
+3V3: R319.1; also elsewhere on the board
BD_N: D302.3, EDBG.A9 (DMHS), J300.D-, R315.1
BD_P: D302.2, EDBG.A8 (DPHS), J300.D+, R316.1
DGI_GPIO0: R307.1
DGI_GPIO1: R308.1; also elsewhere on the board
DGI_GPIO2: R309.1; also elsewhere on the board
DGI_GPIO3: R310.1; also elsewhere on the board
EDBG_ADC0: EDBG.K10 (PA21/PX22); also elsewhere on the board
EDBG_FORCE_BOOT: EDBG.H9 (PA20/PX18), TP301.X
EDBG_JTAG_TCK: EDBG.K9 (TCK), J301.1
EDBG_JTAG_TDI: EDBG.K8 (TDI), J301.9
EDBG_JTAG_TDO: EDBG.J8 (TDO), J301.3
EDBG_JTAG_TMS: EDBG.H7 (TMS), J301.5
EDBG_RESET_N: EDBG.J9 (RESET_N), J301.6
GND: C300.2, C301.2, C302.2, C303.1, C304.2, C305.2, C306.2, C307.2, C308.2, C309.2, C310.2, C311.2, C312.2, C313.2, C314.2, C315.2, D302.1, EDBG.B10 (GNDPLL), EDBG.C3 (GNDIO), EDBG.C8 (GNDIO1), EDBG.E2 (GNDIO2), EDBG.E6 (GNDIO3), EDBG.F5 (GNDIO4), EDBG.F10 (GNDCORE), EDBG.H3 (GNDIO5), EDBG.H8 (GNDANA), J300.GND, J301.2, J301.10, Q300.1 (S), Q300.4 (S), R303.1, R304.1, R317.1, R318.1, TP300.X; also elsewhere on the board
MISO: R311.2; also elsewhere on the board
MOSI: R312.2; also elsewhere on the board
unnamed: D300.C, Q300.6 (D), R303.2
unnamed: D301.C, Q300.3 (D)
unnamed: C303.2, J300.SHLD1 (SH), J300.SHLD2 (SH), J300.SHLD3 (SH), J300.SHLD4 (SH), J300.SHLD5 (SH), J300.SHLD6 (SH), R318.2
unnamed: C308.1, F300.1, L300.2
unnamed: EDBG.B9 (DMF_S), R315.2
unnamed: EDBG.B8 (DPF_S), R316.2
unnamed: C302.1, EDBG.C7 (USB_VBIAS), R317.2
unnamed: C301.1, EDBG.A6 (PC03), X300.1 (C1)
unnamed: C300.1, EDBG.A5 (PC02), X300.3 (C2)
unnamed: C305.1, C306.1, EDBG.E10 (VDDCORE)
unnamed: C304.1, EDBG.J6 (VDDANA), L301.2
unnamed: EDBG.K2 (PX27), R311.1
unnamed: EDBG.K3 (PX28), R312.1
unnamed: EDBG.J4 (PX29), R313.1
unnamed: EDBG.G5 (PX30), R314.1
unnamed: EDBG.C9 (PA11), R310.2
unnamed: EDBG.C10 (PA10), R309.2
unnamed: EDBG.D8 (PA09), R308.2
unnamed: EDBG.F8 (PA08), R307.2
unnamed: EDBG.E9 (PA04), R306.2
unnamed: EDBG.F9 (PA03), R305.2
unnamed: D300.A, R301.1
unnamed: D301.A, R302.1
POWER_LED_CTRL: EDBG.K4 (PX32/PX15), Q300.2 (G), R300.1
RXD: R306.1; also elsewhere on the board
SAMD21_RESET: EDBG.B4 (PA29); also elsewhere on the board
SCK: R313.2; also elsewhere on the board
SCL: EDBG.F7 (PA26/PB05); also elsewhere on the board
SDA: EDBG.G7 (PA12/PA25); also elsewhere on the board
SS: R314.2; also elsewhere on the board
STATUS_LED_CTRL: EDBG.F1 (PX59/PX19), Q300.5 (G), R304.2
SWCLK: EDBG.D6 (PB07); also elsewhere on the board
SWDIO: EDBG.C5 (PB09); also elsewhere on the board
TARGET_RESET_SENSE: EDBG.H2 (PX21); also elsewhere on the board
TXD: R305.1; also elsewhere on the board
VCC_EDBG_3V3: C309.1, C310.1, C311.1, C312.1, C313.1, C314.1, C315.1, EDBG.B5 (VDDIO), EDBG.B6 (VDDIO1), EDBG.D9 (VDDIN), EDBG.D10 (VDDIN1), EDBG.E5 (VDDIO2), EDBG.F2 (VDDIO3), EDBG.F6 (VDDIO4), EDBG.J5 (VDDIO5), J301.4, L301.1, R300.2, R301.2, R302.2, R319.2
VCC_EDBG_USB: EDBG.A10 (USB_VBUS), F300.2; also elsewhere on the board
XVCC: C307.1, D302.4, J300.VBUS (VUSB), L300.1

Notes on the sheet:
Mounting R303 permanently enables the power LED

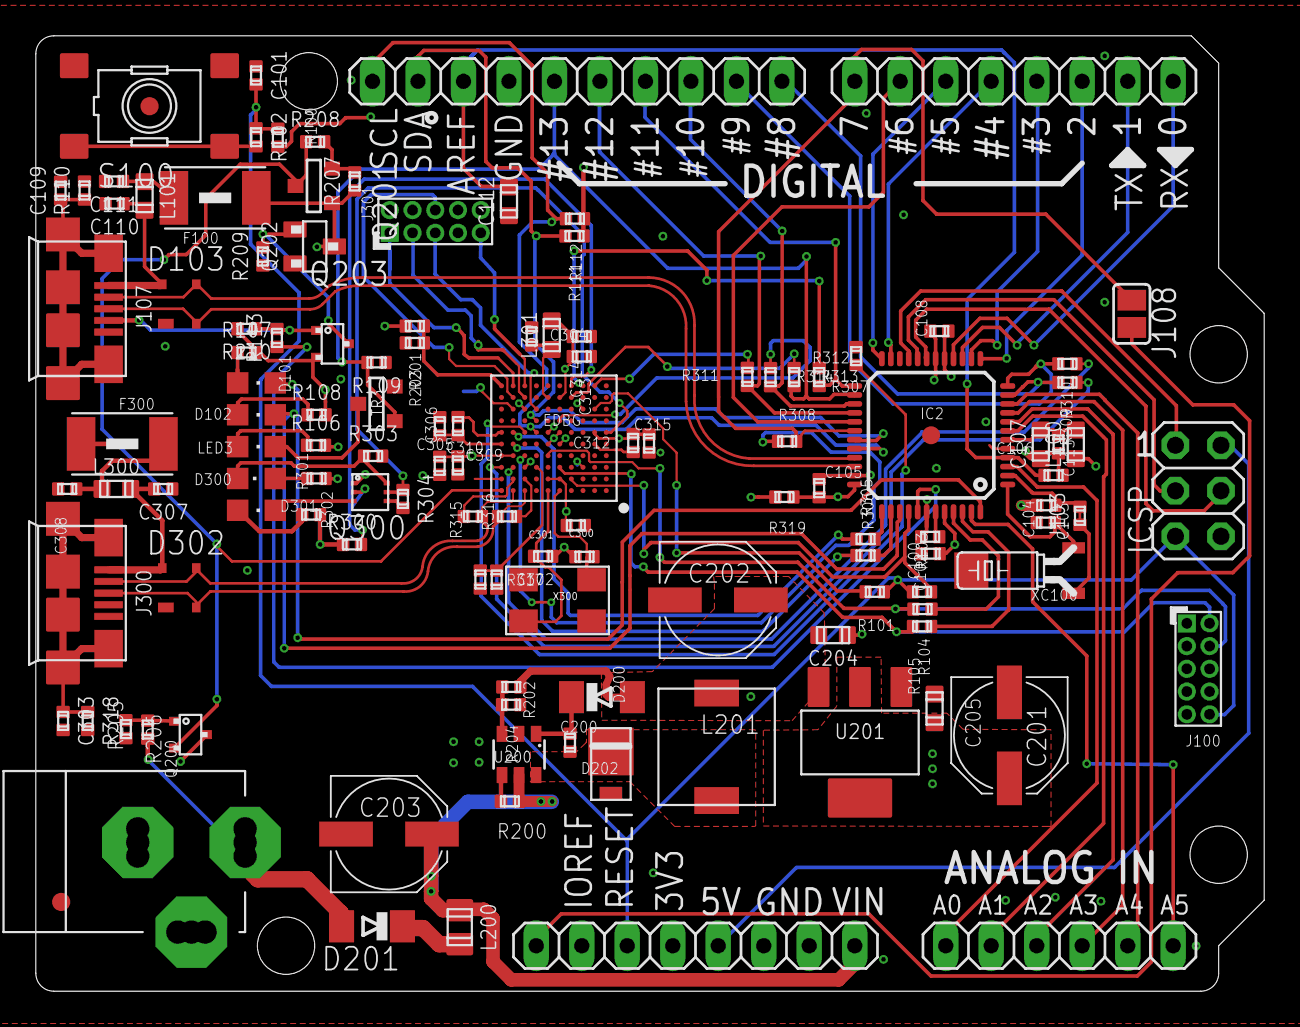
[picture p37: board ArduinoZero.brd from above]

Board: 4 copper layers, 68.6 x 53.3 mm, 128 parts (0 on the bottom side), 104 nets.

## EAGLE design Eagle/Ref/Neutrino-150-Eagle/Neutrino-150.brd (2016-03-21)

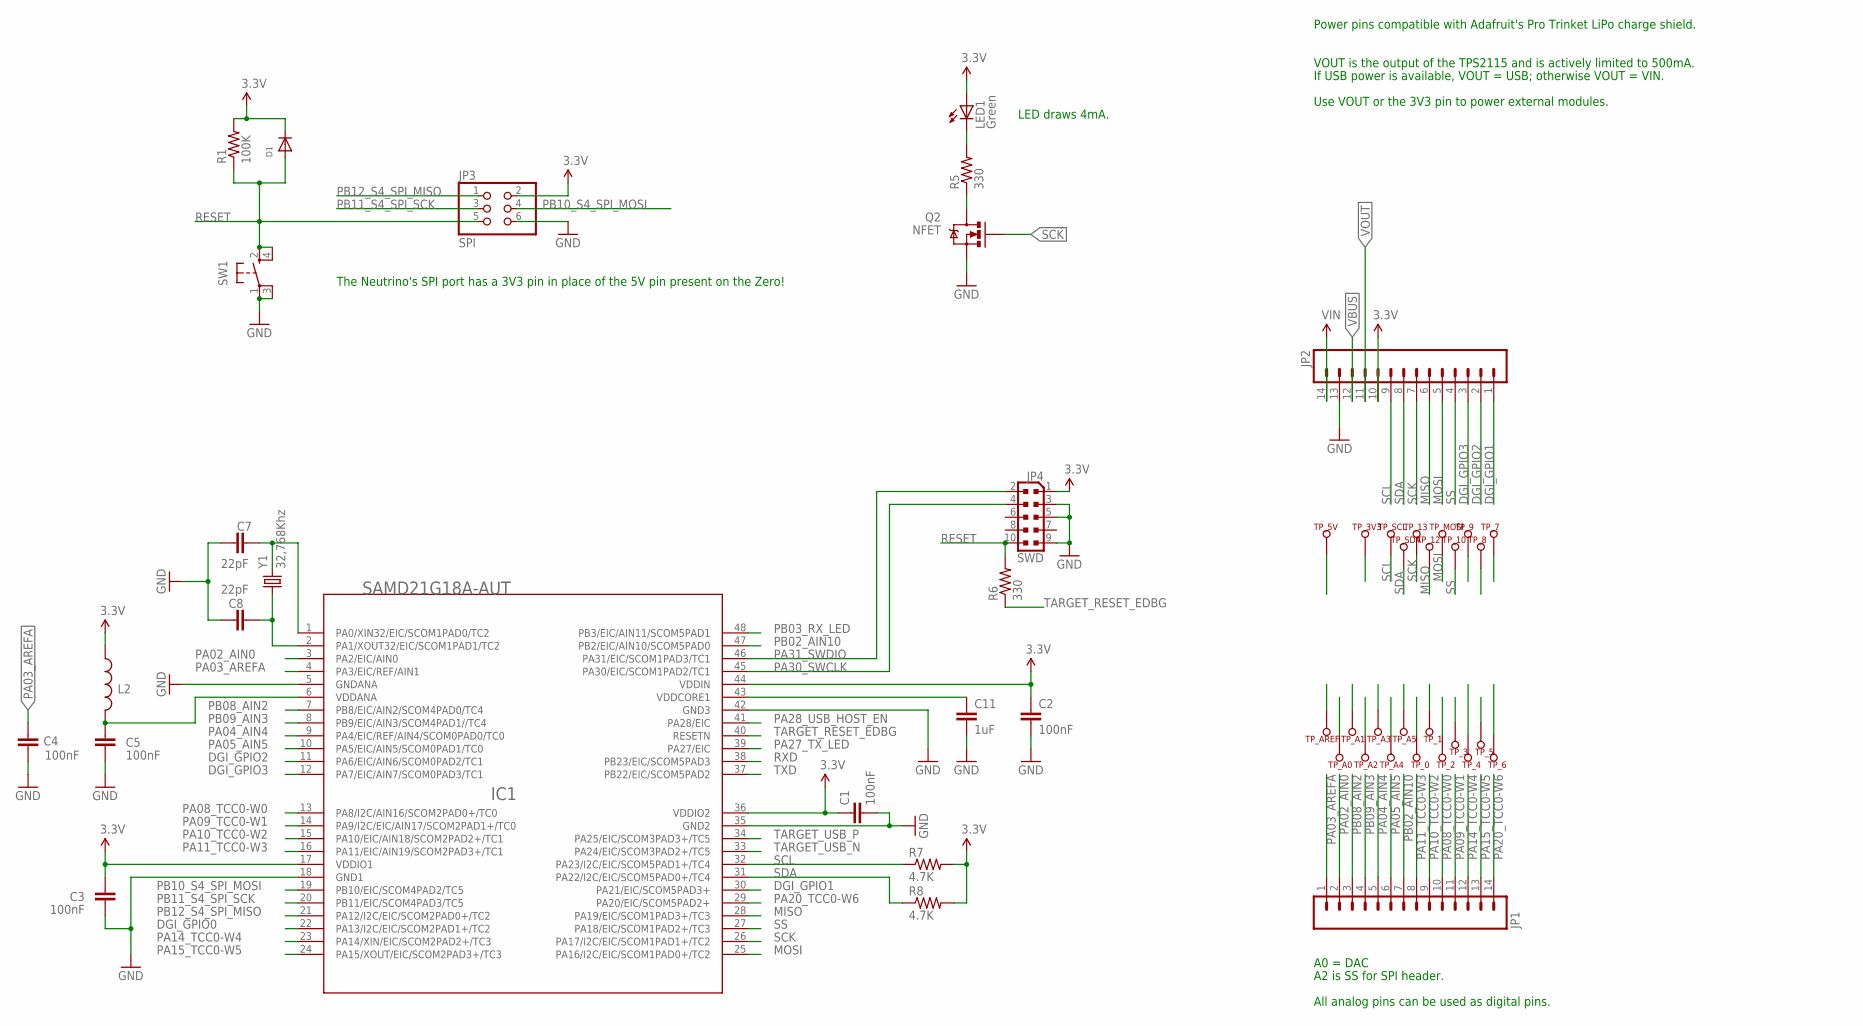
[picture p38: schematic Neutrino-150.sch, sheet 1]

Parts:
C1, C2, C3, C4, C5: 100nF; 0402-CAP
C7, C8: 22pF; 0402-CAP
C11: 1uF; 0402-CAP
D1: DIODESOD-523; SOD-523
IC1: SAMD21G18A-AUT; INTEGRATEDCIRCUITS_TQFP48-7X7
JP1, JP2: M14NOSILK_SMALLPADS; 1X14_NO_SILK_SMALLPADS
JP3: SPI; CONNETTORI_2X03
JP4: SWD; CONNETTORI_PINHEAD-2X5-P127
L2: INDUCTOR0603-TDK; 0603-TDK
LED1: Green; CHIPLED_0805
Q2: NFET; SOT323
R1: 100K; R0402-VISHAY
R5, R6: 330; R0402-VISHAY
R7, R8: 4.7K; R0402-VISHAY
SW1: SPST_TACT-KMR2; KMR2
TP_0, TP_1, TP_2, TP_3, TP_3V3, TP_4, TP_5, TP_5V, TP_6, TP_7, TP_8, TP_9, TP_10, TP_12, TP_13: TP_SP; TP-SP
TP_A0, TP_A1, TP_A2, TP_A3, TP_A4, TP_A5: TP_SP; TP-SP
TP_AREF: TP_SP; TP-SP
TP_MOSI: TP_SP; TP-SP
TP_SCL: TP_SP; TP-SP
TP_SDA: TP_SP; TP-SP
Y1: 32,768Khz; CRYSTAL-SMD-2.0X1.2

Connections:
3.3V: C1.1, C2.1, C3.2, D1.K (C), IC1.17 (VDDIO1), IC1.36 (VDDIO2), IC1.44 (VDDIN), JP2.10, JP3.2, JP4.1, L2.1, LED1.A, R1.2, R7.2, R8.2, TP_3V3.X; also elsewhere on the board
+5V: TP_5V.X
DGI_GPIO0: IC1.22 (PA13/I2C/EIC/SCOM2PAD1+/TC2)
DGI_GPIO1: IC1.30 (PA21/EIC/SCOM5PAD3+), JP2.1, TP_7.X
DGI_GPIO2: IC1.11 (PA6/EIC/AIN6/SCOM0PAD2/TC1), JP2.2, TP_8.X
DGI_GPIO3: IC1.12 (PA7/EIC/AIN7/SCOM0PAD3/TC1), JP2.3, TP_9.X
GND: C1.2, C2.2, C3.1, C4.2, C5.2, C7.1, C8.1, C11.2, IC1.5 (GNDANA), IC1.18 (GND1), IC1.35 (GND2), IC1.42 (GND3), JP2.13, JP3.6, JP4.3, JP4.5, JP4.9, Q2.2 (S), SW1.1, SW1.3 (P1); also elsewhere on the board
MISO: IC1.28 (PA19/EIC/SCOM1PAD3+/TC3), JP2.6, TP_12.X
MOSI: IC1.25 (PA16/I2C/EIC/SCOM1PAD0+/TC2), JP2.5, TP_MOSI.X
unnamed: LED1.C, R5.2
unnamed: Q2.3 (D), R5.1
PA00_XIN32: C7.2, IC1.1 (PA0/XIN32/EIC/SCOM1PAD0/TC2), Y1.2
PA01_XOUT32: C8.2, IC1.2 (PA1/XOUT32/EIC/SCOM1PAD1/TC2), Y1.1
PA02_AIN0: IC1.3 (PA2/EIC/AIN0), JP1.2, TP_A0.X
PA03_AREFA: C4.1, IC1.4 (PA3/EIC/REF/AIN1), JP1.1, TP_AREF.X
PA04_AIN4: IC1.9 (PA4/EIC/REF/AIN4/SCOM0PAD0/TC0), JP1.5, TP_A3.X
PA05_AIN5: IC1.10 (PA5/EIC/AIN5/SCOM0PAD1/TC0), JP1.6, TP_A4.X
PA08_TCC0-W0: IC1.13 (PA8/I2C/AIN16/SCOM2PAD0+/TC0), JP1.10, TP_2.X
PA09_TCC0-W1: IC1.14 (PA9/I2C/EIC/AIN17/SCOM2PAD1+/TC0), JP1.11, TP_3.X
PA10_TCC0-W2: IC1.15 (PA10/EIC/AIN18/SCOM2PAD2+/TC1), JP1.9, TP_1.X
PA11_TCC0-W3: IC1.16 (PA11/EIC/AIN19/SCOM2PAD3+/TC1), JP1.8, TP_0.X
PA14_TCC0-W4: IC1.23 (PA14/XIN/EIC/SCOM2PAD2+/TC3), JP1.12, TP_4.X
PA15_TCC0-W5: IC1.24 (PA15/XOUT/EIC/SCOM2PAD3+/TC3), JP1.13, TP_5.X
PA20_TCC0-W6: IC1.29 (PA20/EIC/SCOM5PAD2+), JP1.14, TP_6.X
PA27_TX_LED: IC1.39 (PA27/EIC)
PA28_USB_HOST_EN: IC1.41 (PA28/EIC); also elsewhere on the board
PA30_SWCLK: IC1.45 (PA30/EIC/SCOM1PAD2/TC1), JP4.4
PA31_SWDIO: IC1.46 (PA31/EIC/SCOM1PAD3/TC1), JP4.2
PB02_AIN10: IC1.47 (PB2/EIC/AIN10/SCOM5PAD0), JP1.7, TP_A5.X
PB03_RX_LED: IC1.48 (PB3/EIC/AIN11/SCOM5PAD1)
PB08_AIN2: IC1.7 (PB8/EIC/AIN2/SCOM4PAD0/TC4), JP1.3, TP_A1.X
PB09_AIN3: IC1.8 (PB9/EIC/AIN3/SCOM4PAD1//TC4), JP1.4, TP_A2.X
PB10_S4_SPI_MOSI: IC1.19 (PB10/EIC/SCOM4PAD2/TC5), JP3.4
PB11_S4_SPI_SCK: IC1.20 (PB11/EIC/SCOM4PAD3/TC5), JP3.3
PB12_S4_SPI_MISO: IC1.21 (PA12/I2C/EIC/SCOM2PAD0+/TC2), JP3.1
RESET: D1.A, JP3.5, JP4.10, R1.1, R6.2, SW1.2 (S), SW1.4 (S1)
RXD: IC1.38 (PB23/EIC/SCOM5PAD3)
SCK: IC1.26 (PA17/I2C/EIC/SCOM1PAD1+/TC2), JP2.7, Q2.1 (G), TP_13.X
SCL: IC1.32 (PA23/I2C/EIC/SCOM5PAD1+/TC4), JP2.9, R7.1, TP_SCL.X
SDA: IC1.31 (PA22/I2C/EIC/SCOM5PAD0+/TC4), JP2.8, R8.1, TP_SDA.X
SS: IC1.27 (PA18/EIC/SCOM1PAD2+/TC3), JP2.4, TP_10.X
TARGET_RESET_EDBG: IC1.40 (RESETN), R6.1
TARGET_USB_N: IC1.33 (PA24/EIC/SCOM3PAD2+/TC5); also elsewhere on the board
TARGET_USB_P: IC1.34 (PA25/EIC/SCOM3PAD3+/TC5); also elsewhere on the board
TXD: IC1.37 (PB22/EIC/SCOM5PAD2)
VBUS: JP2.12; also elsewhere on the board
VDDANA: C5.1, IC1.6 (VDDANA), L2.2
VDDCORE: C11.1, IC1.43 (VDDCORE1)
VIN: JP2.14; also elsewhere on the board
VOUT: JP2.11; also elsewhere on the board

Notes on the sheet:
A0 = DAC
All analog pins can be used as digital pins.
Power pins compatible with Adafruit's Pro Trinket LiPo charge shield.
LED draws 4mA.
The Neutrino's SPI port has a 3V3 pin in place of the 5V pin present on the Zero!
A2 is SS for SPI header.
VOUT is the output of the TPS2115 and is actively limited to 500mA.
If USB power is available, VOUT = USB; otherwise VOUT = VIN.
Use VOUT or the 3V3 pin to power external modules.

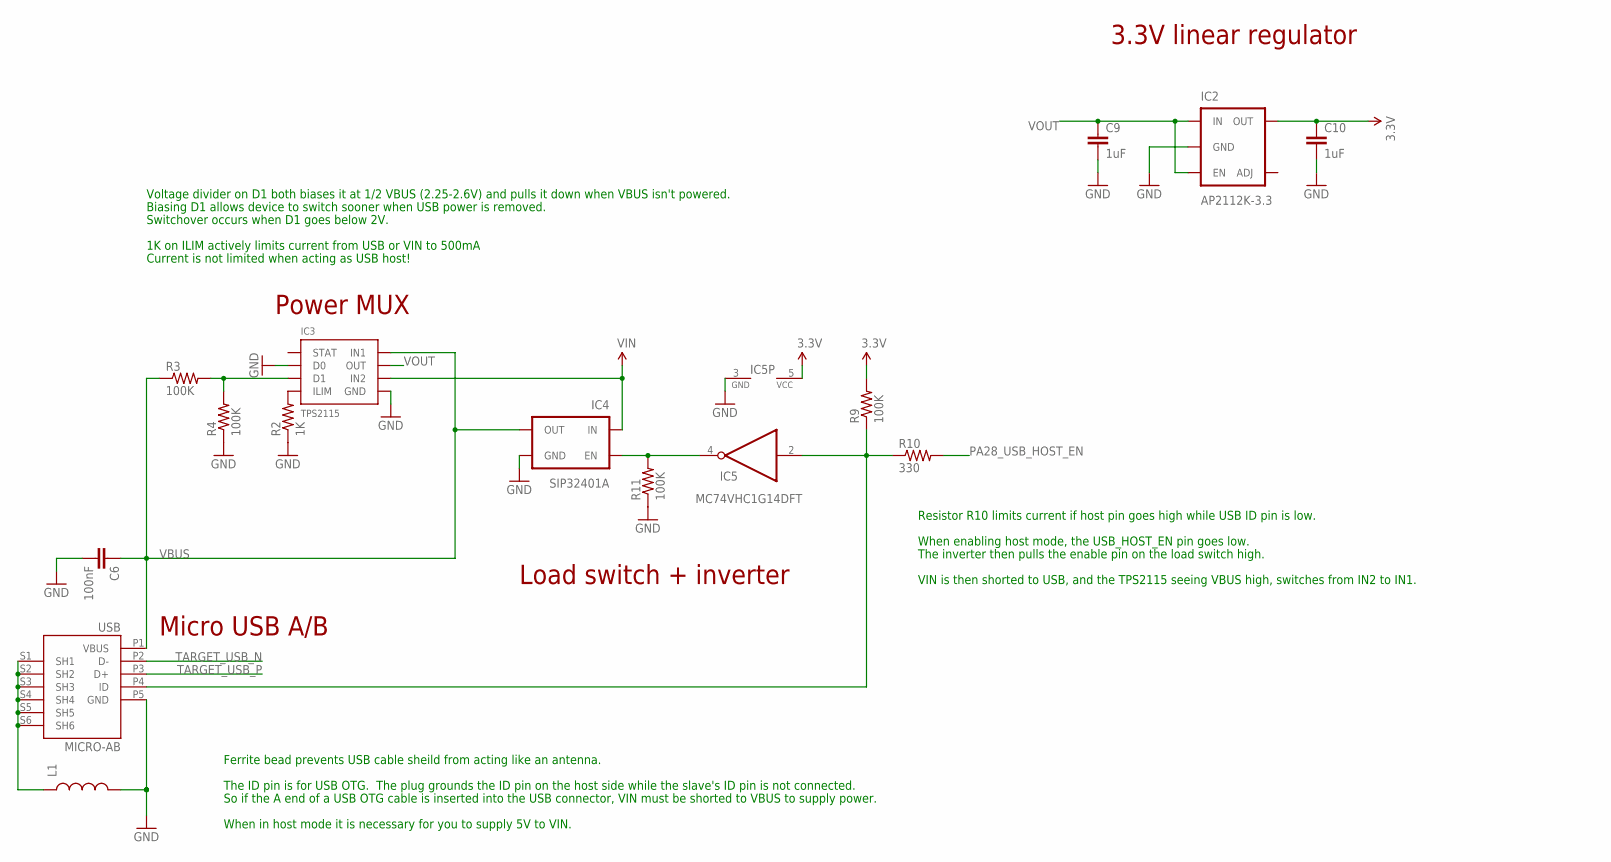
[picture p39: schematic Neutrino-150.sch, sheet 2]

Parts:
C6: 100nF; 0402-CAP
C9, C10: 1uF; 0402-CAP
IC2: AP2112K-3.3; SOT23-5
IC3: TPS2115; 8-VDFN
IC4: SIP32401A; TDFN4
IC5: MC74VHC1G14DFT; SC70-5
L1: INDUCTOR0603-TDK; 0603-TDK
R2: 1K; R0402-VISHAY
R3, R4, R9, R11: 100K; R0402-VISHAY
R10: 330; R0402-VISHAY
USB: MICRO-AB; MOLEX_USB_MICRO_AB

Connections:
3.3V: C10.1, IC2.5 (OUT), IC5.5 (VCC), R9.2; also elsewhere on the board
D1: IC3.3 (D1), R3.2, R4.2
GND: C6.2, C9.2, C10.2, IC2.2 (GND), IC3.2 (D0), IC3.5 (GND), IC3.P0 (GND), IC3.V0 (GND), IC3.V1 (GND), IC3.V2 (GND), IC3.V3 (GND), IC3.V4 (GND), IC4.0 (GND), IC4.2 (GND), IC5.3 (GND), L1.2, R2.1, R4.1, R11.1, USB.P5 (GND); also elsewhere on the board
IC4_EN: IC4.4 (EN), IC5.4 (O), R11.2
ILIM: IC3.4 (ILIM), R2.2
unnamed: IC5.2 (I), R9.1, R10.1, USB.P4 (ID)
PA28_USB_HOST_EN: R10.2; also elsewhere on the board
SHIELD: L1.1, USB.S1 (SH1), USB.S2 (SH2), USB.S3 (SH3), USB.S4 (SH4), USB.S5 (SH5), USB.S6 (SH6)
TARGET_USB_N: USB.P2 (D-); also elsewhere on the board
TARGET_USB_P: USB.P3 (D+); also elsewhere on the board
VBUS: C6.1, IC3.8 (IN1), IC4.1 (OUT), R3.1, USB.P1 (VBUS); also elsewhere on the board
VIN: IC3.6 (IN2), IC4.3 (IN); also elsewhere on the board
VOUT: C9.1, IC2.1 (IN), IC2.3 (EN), IC3.7 (OUT); also elsewhere on the board

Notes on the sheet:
Micro USB A/B
Ferrite bead prevents USB cable sheild from acting like an antenna.
The ID pin is for USB OTG. The plug grounds the ID pin on the host side while the slave's ID pin is not connected.
So if the A end of a USB OTG cable is inserted into the USB connector, VIN must be shorted to VBUS to supply power.
3.3V linear regulator
When in host mode it is necessary for you to supply 5V to VIN.
1K on ILIM actively limits current from USB or VIN to 500mA
Voltage divider on D1 both biases it at 1/2 VBUS (2.25-2.6V) and pulls it down when VBUS isn't powered.
Current is not limited when acting as USB host!
Biasing D1 allows device to switch sooner when USB power is removed.
Switchover occurs when D1 goes below 2V.
When enabling host mode, the USB_HOST_EN pin goes low.
Resistor R10 limits current if host pin goes high while USB ID pin is low.
Load switch + inverter
The inverter then pulls the enable pin on the load switch high.
Power MUX
VIN is then shorted to USB, and the TPS2115 seeing VBUS high, switches from IN2 to IN1.


Board: 2 copper layers, 36.8 x 17.8 mm, 64 parts (0 on the bottom side), 49 nets.

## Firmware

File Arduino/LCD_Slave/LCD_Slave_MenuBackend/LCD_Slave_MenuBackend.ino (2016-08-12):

/***************************************************************
                    Included libraries 
****************************************************************/

//#include <MenuBackend.h> // Generic menu management lib
#include <LiquidCrystal.h> // LCD display lib
#include <SPI.h> // SPI communication lib

/***************************************************************
                    Constants & Definitions
****************************************************************/

#define LCDD7  A6
#define LCDD6  12
#define LCDD5  6
#define LCDD4  8
#define LCDE   9
#define LCDRS  10

LiquidCrystal lcd(LCDRS,LCDE,LCDD4,LCDD5,LCDD6,LCDD7);

#define MAX_PARAM  52

#define PARAM_TEMP_LIQ             0   // temperature of the solution
#define PARAM_TEMP_PCB             1   // temperature of the heating plate
#define PARAM_WEIGHT               2   // in gr
#define PARAM_WEIGHT_FACTOR        15  // Weight calibration: conversion factor digital -> gr (weight=FACTOR*dig_unit)
#define PARAM_WEIGHT_OFFSET        16  // Weight calibration: digital offset value when bioreactor is empty
#define PARAM_STEPPER_SPEED        18  // motor speed, parameter S (!!!!!TO BE REPROGRAMMED IN RPM!!!!!!!)
#define PARAM_WEIGHT_STATUS        23  // current STATUS // BBBAAAAA AAAAAAAA : A = wait time in minutes, B = status
#define PARAM_STATUS               25  
#define PARAM_TEMP_TARGET          26  // target temperature of the liquid
#define PARAM_TEMP_REG_TIME        28  //in [ms]
#define PARAM_WEIGHT_MIN           29    
#define PARAM_WEIGHT_MAX           30  
#define PARAM_SEDIMENTATION_TIME   35  // MINUTES to wait without rotation before emptying
#define PARAM_FILLED_TIME          36  // MINUTES to stay in the filled state


#define ENCODER_CLOCKWISE      0
#define ENCODER_ANTI_CLOCKWISE 1
#define ENCODER_BUTTON         7
#define INT_CLOCKWISE          2
#define INT_ANTI_CLOCKWISE     3
#define INT_BUTTON             4  

#define SPI_OUT_BUF_SIZE    4

/***************************************************************
                    Global Variables
****************************************************************/

///////////////////////
// Menu system
///////////////////////

typedef struct{
   int value;
   char* item_name;   
} menuItem;

menuItem param [MAX_PARAM];

///////////////////////
// SPI and data parsing
///////////////////////

byte out_buf [SPI_OUT_BUF_SIZE];                  // buffer for output to motherboard 
boolean write_to_master=false;                    // flag indicating if their is something to send to the motherboard
boolean is_start=false;                           // flag indicating if it's the beginning of the communication with the motherboard

byte buf [2*MAX_PARAM+2];     // buffer for input from motherboard
volatile byte pos;
uint16_t param [MAX_PARAM];

///////////////////////
// Encoder Values
///////////////////////

volatile unsigned int encoderTempValue   = 0;  // a counter to store a temporary value before to set it
volatile unsigned int encoderLastValue   = 0;  // a counter to store a previous temporary value 

///////////////////////
// flags
///////////////////////

volatile boolean process_it=false;
volatile boolean first_return=false;    
static boolean rotating=false;         // debounce management
static boolean pushing  =true;         // debounce management
// interrupt service routine variables
boolean A_set = false;              
boolean B_set = false;


/***************************************************************
                    SPI related routines
****************************************************************/

void SPI_slave_init()
{
  pinMode(SS,INPUT);     //switch the slave select pin to input mode
  digitalWrite(SS,HIGH); //turn on internal pull-up
  // turn on SPI in slave mode
  SPCR |= bit (SPE);
  SPI.setDataMode(SPI_MODE0);
  SPI.setBitOrder(MSBFIRST);
  // have to send on master in, *slave out*
  pinMode(MISO, OUTPUT);
  // get ready for an interrupt 
  pos = 0;   // buffer empty
  process_it = false;
  // now turn on interrupts
  SPI.attachInterrupt();
}

void buffer_parser(){
 //  epoch=((buf[4]<<24) + (buf[5]<<16) + (buf[6]<<8) + buf[7]);
  for(int i=0;i<26;i++)
    param[i]=((buf[2*i]<<8)&(0xFF00))+(buf[2*i+1]&(0x00FF));  
}

/**
 * Set parameter on motherboard through SPI communication. 
 * int parameter : location of parameter in param list. Use defined parameters.
 * int value : value to be set for the given parameter. 
 */
void sendParameter(int parameter, int value){
  out_buf[0]=1;                                     // Start transmission with non_null byte
  out_buf[1]=(byte)parameter;                       // Number of parameter to set
  out_buf[2]=(byte)((value>>8)&(0x00FF));           // Value of parameter
  out_buf[3]=(byte)(value&(0x00FF));
  write_to_master = true;                           // notify SPI interrupt that it can start sending bytes as soon as the transmission starts
}

/***************************************************************
                    LCD Display routines
****************************************************************/

void LCD_println(int line_num, char* text){
  lcd.setCursor(0, line_num);
  lcd.print(text);  
}

void LCD_printItem(){}
/***************************************************************
                    Setup & Loop routines
****************************************************************/

void setup() {
  pinMode(ENCODER_CLOCKWISE, INPUT); 
  pinMode(ENCODER_ANTI_CLOCKWISE, INPUT); 
  pinMode(ENCODER_BUTTON, INPUT);
  // turn on iinternal pullup resistors
  digitalWrite(ENCODER_CLOCKWISE, HIGH);
  digitalWrite(ENCODER_ANTI_CLOCKWISE, HIGH);
  digitalWrite(ENCODER_BUTTON, HIGH);
  // attach interrupt routines
  attachInterrupt(INT_CLOCKWISE, doEncoderA, CHANGE);
  attachInterrupt(INT_ANTI_CLOCKWISE, doEncoderB, CHANGE);
  attachInterrupt(INT_BUTTON, doEncoderButton, CHANGE);
  //Serial communication start
  Serial.begin(9600);  
  SPI_slave_init();
  lcd.begin(20, 4);
  LCD_println(0, "Test");
}

void loop() {
  // put your main code here, to run repeatedly:

}

/***************************************************************
                    Interrupt routines
****************************************************************/
// Interrupt on A changing state
void doEncoderA(){
//  delay(10);
  if ( rotating ) 
    delay(20);//debounce
    if( digitalRead(ENCODER_CLOCKWISE) != A_set ) {  // debounce once more
      A_set = !A_set;
      if ( A_set && !B_set ) 
        encoderTempValue++;
    }
    rotating = false;  // no more debouncing until loop() hits again
}

// Interrupt on B changing state, same as A above
void doEncoderB(){
//  delay(10);
  if ( rotating )
    delay(20);
    if( digitalRead(ENCODER_ANTI_CLOCKWISE) != B_set ) {
      B_set = !B_set;
      //  adjust counter - 1 if B leads A
      if( B_set && !A_set ) 
        encoderTempValue--;

    rotating = false;
  }
}

// Interrupt on B changing state, same as A above
void doEncoderButton(){
  if (pushing){
    pushing=false;     //debouncer  
  }
  else 
    pushing=true;
    
  delay(10);
}


// SPI interrupt routine
ISR (SPI_STC_vect)
{
  byte c = SPDR;  // grab byte from SPI Data Register
  
  /////////////////////
  // Read entering byte
  /////////////////////
  
  // add to buffer if room
  if (pos < sizeof(buf))
  {
     buf [pos] = c;                   //add byte to buffer
                                        // example: newline means time to process buffer
    if (c == '\n')
      first_return=true;
    if (c=='\n' && first_return==true)  
      process_it = true;
    else
      first_return=false; 
  }  // end of room available

  //////////////
  // Send answer
  //////////////

  if (!pos){                            // start sending out bytes when the first byte is received
    is_start = true;  
  }
  
  if (is_start && write_to_master){     // send bytes if begining of communication and if their is something...
    SPDR = out_buf[pos];                // ...new to send to the master  
    Serial.print("Sent a byte: ");
    Serial.println(out_buf[pos]);
    if(pos+1>=SPI_OUT_BUF_SIZE){
      write_to_master=false;
      is_start = false;
    }
  }
  else
    SPDR = 0;

  pos++;
}  // end of interrupt routine SPI_STC_vect

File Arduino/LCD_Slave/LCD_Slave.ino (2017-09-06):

/**********************************************************************************************
   LCD_SLAVE is an Arduino programm conceived for the Open-source bioreactor programm.
   This code features a programm to run on the LCD annex board to the project. It features:

   - SPI-communication with the main board in order to be able to set parameters without help
     from the computer Serial
   - A graphic menu interface allowing to view access certain commands from the bioreactor.
     The menu is architectured as such:

      MENU_SELECTOR
        |
        |- MENU_SENSOR
        |
        |- MENU_CONFIG ------|
        |               MENU_SET_VALUE
        |
        |- MENU_CALIB

   With the menus containing:

   -> MENU_SELECTOR: Home menu.
   -> MENU_SENSOR: Visualizing useful parameters. Display only. Can't be modified.
                    - Stepper RPM
                    - Current temperature
                    - Current weight
   -> MENU_CONFIG: List of settings that can be updated to set-up the bioreactor.
                    - Stepper speed
                    - Target temperature
                    - Max and min weight
                    - Sedimentation and filled times
   -> MENU_SET_VALUE: Choose new value for configurable parameter and parse and send it to
                      BioMain programm.
   -> MENU_CALIB: Weight calibration menu.
                    - Tare calibration
                    - 1kg calibration
 **********************************************************************************************/

#include <LiquidCrystal.h>
#include <SPI.h>
#include "LCD_Slave.h"

// initialize the lib with the nbr of the interface pins
LiquidCrystal lcd(LCDRS, LCDE, LCDD4, LCDD5, LCDD6, LCDD7);

//-------------------------------------------------------------------------------------------------------------------------//

/*************************
   CONSTANTS DEFINITIONS
 *************************/

// MENU POSITION LABELS
// --------------------

volatile byte encoderCurrentMenu = MENU_SELECTOR;     // Page we are currently in
volatile byte encoderPreviousMenu = MENU_SELECTOR;    // Previous page
volatile unsigned encoderSelector = 0;                // Cursor position in our menu
volatile unsigned int encoderPreviousSelection = 0;   // Cursor position in previous menu

// MENU AND VALUES REFRESH
// -----------------------

static boolean refreshMenu = true;    // Menu is only refreshed when button is pushed or in sensors menu when the wheel is turned
static boolean processIt = true;      // Check if values have been changed by either SPI interrupt or user param modification

// DEBOUNCE AND ISR VARIABLES
// --------------------------

static boolean rotating = false;  // debounce management
static boolean pushing  = true;   // debounce management
boolean A_set = false;            // ISR variable
boolean B_set = false;            // ISR variable
boolean accelerationMode = false; // When button is turned fast, variables change faster in Values setting menu
long lastEvent = millis();        // Timecode of previous rotating event: utilitary for acceleration mode

// SPI COMMUNICATION WITH MASTER
// -----------------------------

byte outBuf [OUT_BUF_SIZE];       // output SPI buffer
boolean writeToMaster = false;    // flag indicating if there is something to send
boolean isStart = false;          // flag indicating if beginning of the COM
byte buf [2 * MAX_PARAM + 1];     // buffer for input from motherboard : maxparams + XOR
volatile byte pos;                // position of incoming byte in SPI buffer
uint16_t param [MAX_PARAM] = {0}; // Table to stock parameters values, initialized to an array of 0
byte buffSize = 0;                // Size of incomming buffer

//-------------------------------------------------------------------------------------------------------------------------//

/***********************
   PARAMETER UTILITIES
 ***********************/

typedef struct {
  char* paramName = 0;
  int paramNameLength = 0;
  int paramNum = 0; // paramNum, gives the parameters number in the parameters table (bioMain)
} parameter;

parameter * configMenuParams [MAX_CONFIG_PARAM];  // Configurable parameters
parameter * weightMenuParams [MAX_WEIGHT_PARAM];  // Weight calib parameters

byte weightParamCalib = 0;                        // Weight parameter to calibrate

// Utilitary function: Prints parameter infos on Serial
void printParam(int pos) {
  if (pos >= 0 && pos < MAX_CONFIG_PARAM) {
    parameter * param = configMenuParams[pos];
    Serial.print(F("ParamName:"));
    Serial.println(param->paramName);
    Serial.print(F("Param#:"));
    Serial.println(param->paramNum);
  } else {
    Serial.println(F("Err: pos of config variable out of range"));
  }
}

// Add new parameter to table of parameters
void addConfigParam(int pos, char * id, int idLength, int number) {

  if (pos >= 0 && pos < MAX_CONFIG_PARAM) {
    parameter * newParam = (parameter *) malloc(idLength + 2 * sizeof(int)); // memory allocation
    newParam->paramName = id;
    newParam->paramNameLength = idLength;
    newParam->paramNum = number;
    configMenuParams[pos] = newParam;

    printParam(pos);
  } else {
    Serial.println(F("Err: pos of config variable is out of range"));
  }
}

// Add new parameter to table of parameters
void addWeightParam(int pos, char * id, int idLength, int number) {

  if (pos >= 0 && pos < MAX_WEIGHT_PARAM) {
    parameter * newParam = (parameter *) malloc(idLength + 2 * sizeof(int)); // memory allocation
    newParam->paramName = id;
    newParam->paramNameLength = idLength;
    newParam->paramNum = number;
    weightMenuParams[pos] = newParam;

    printParam(pos);
  } else {
    Serial.println(F("Err: pos of config variable is out of range"));
  }
}

//-------------------------------------------------------------------------------------------------------------------------//

/*********************
   DISPLAY UTILITIES
 *********************/

// MENU DISPLAYS
// -------------

// Main menu display function. Reroutes to each different menu
void displayMenu()
{
  switch (encoderCurrentMenu) {
    case MENU_SELECTOR:
      displayMenuSelector();
      break;
    case MENU_SENSOR:
      displayMenuSensor();
      break;
    case MENU_CONFIG:
      displayMenuConfig();
      break;
    case MENU_CALIBRATION:
      displayMenuCalibr();
      break;
    case MENU_WEIGHT_CONFIRM:
      displayWeightConfirm();
      break;
    default:
      return;
  }
  refreshMenu = false;
}
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

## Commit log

2016-02-28 First version
    [Bertha_v4_1.brd, Bertha_v4_1.sch, Bio_v4_LCD.brd, Bio_v4_LCD.sch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]
2016-03-07 started pH conducto PCB board
    [BOM_phMeter v4.2.csv, pH_v5_0.brd, pH_v5_0.sch, phMeter v4.2.brd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]
2016-03-07 Update value label position
    [Bio_v4_LCD.brd, Bio_v4_LCD.sch]
2016-03-12 completed the readme for current status of the project, added the arduino Zero reference Eagle files
    [ArduinoZero.brd, ArduinoZero.sch]
2016-03-12 added reference to the neutrino board
    [Neutrino-150.brd, Neutrino-150.sch]
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2016-03-22 added Flash SPI selection pin, cleared useless code, modified parameter table (1st revision), started the design revision toward v4.2
    [Bertha_v4_2.brd, Bertha_v4_2.sch]
2016-03-23 added CS for memory, not working
    [Bertha_v4_1.brd]
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2016-04-13 swapped flex connector on LCD SPI, changed D11 pin by the SS/RXLED pin instead, removed SPI pull-up + diode
    [Bio_v4_LCD.brd, Bio_v4_LCD.sch, Bio_v4_LCD0_2.brd, Bio_v4_LCD0_2.sch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]
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2016-04-13 Created git file in repository
    First Case Prototype
    [Arduino.SLDPRT, Assembly.SLDASM, Stepper 33.SLDPRT, Stepper 47.SLDPRT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]
2016-04-13 changed read/write rights n CAD folder
    [Arduino.SLDPRT, Assembly.SLDASM, Stepper 33.SLDPRT, Stepper 47.SLDPRT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]
2016-05-19 bioreactor v4.2 revision, Lora Reset pin on D5, operation at 8MHz, 3.3V. The Flex cable is now exporting 12V instead of 5V (careful, not compatible with LCD V0.2 sudo git add --all), I2C ports are on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
    [ArduinoZero.brd, ArduinoZero.sch, Bertha_v4_1.brd, Bertha_v4_1.sch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]
2016-05-24 LCD v1_0, compatible with v4_2 of the main board, 5V generated on board w NCP1117
    [Bio_v4_LCD0_2.brd, Bio_v4_LCD0_2.sch, Bio_v4_LCD0_2_pan.brd, Bio_v4_LCD1_0.brd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]
2016-05-24 panelized LCD board v1_0
    [Bio_v4_LCD1_0_panelized.brd]
2016-06-03 corrected bioreactor board for microcircuitos (0.25mm clearance)
    [Bertha_v4_2.brd, Bertha_v4_2.sch]
2016-06-03 corrected DRC for microcuircuitos on LCD board (0.25mm clearance)
    [Bio_v4_LCD1_0.brd, Bio_v4_LCD1_0.sch, Bio_v4_LCD1_0_panelized.brd]
2016-07-27 CAD files sorted into version folders
    [A Bioreactor v3.SLDASM, A screen.SLDASM, Box Board v1.4.stl, Foot.SLDPRT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]
2016-07-27 CAD Alexandre design
    [Assembly.SLDASM, back face.SLDPRT, back support weight sensor.SLDPRT, bottom face.SLDPRT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]
2016-08-12 Added Documentation and CAD files.
    [BASE.CATProduct, BASE_COUVERCLE_ALU.CATPart, BASE_COUVERCLE_LCD.CATPart, BASE_COUVERCLE_LCD.dxf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]
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2016-10-11 error found on eagle brd, LDO 3V3 was disconnected !, need to regenerate the gerbers !
    [Bertha_v4_2.brd]
2016-10-21 new v4.3, removed bistable control of the stepper, now on pins A0/A1/D8/D9, control sequence must be adapted in the arduino code. Started to work on the ph_V5.0 board, need to add two steppers and th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
    [Bertha_v4_3.brd, Bertha_v4_3.sch, ph_v5.brd, ph_v5.sch]
2016-10-31 started design of the phv5.0 board, conductommetry is still missing, stepper to be rerouted to use one single port would be better !
    [ph_v5.brd, ph_v5.sch]
2016-10-31 ph board v5, need to be checked, to provide pin mapping and gerbers
    [ph_v5.brd, ph_v5.sch]
2016-11-01 finished phv5.0 board, need to dimension correctly the pH resistors and conductometry resistors and capa (not dimensionned yet !! careful not to solder anything)
    [ph_v5.brd, ph_v5.sch]
2016-11-09 reviewed LCD board with fle cable for button
    [Bio_v4_LCD1_1.brd, Bio_v4_LCD1_1.sch, Bio_v4_LCD1_1_pan.brd]
2016-11-09 corrected cupper width for pcbway
    [Bio_v4_LCD1_1_pan.brd]
2016-12-06 added pin mapping csv, reorganized files
    [PinMapping20161206.csv]
2016-12-06 adapted parameters table
    [V4_PARAMS20161206 - Sheet1.csv]
2016-12-06 Rename V4_PARAMS20161206 - Sheet1.csv to V4_PARAMS20161206.csv
    [V4_PARAMS20161206.csv]
2016-12-06 detail on state machines
    [StateMachines.csv]
2016-12-08 corected BCN connector side on phv5
    [ph_v5.brd]
2016-12-08 minor change to the state machines table
    [StateMachines.csv]
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2016-12-12 Added SMA LoRa antenna for 4.3 ref #18, same needs to be done for the pH board
    [Bertha_v4_3.brd, Bertha_v4_3.sch]
2016-12-12 Added SMA LoRa antenna for phV5 board extra mistakes fixed with DRC close #18
    [ph_v5.brd, ph_v5.sch]
2016-12-13 Implemented PID with PWM control ref #13, hack to be performed on V4.3 and anterior corection to be provided on eagle
    [PinMapping20161206.csv, V4_PARAMS20161206.csv]
2016-12-13 exchanged pins D6 and D12 for PID on PWM closes #13
    [Bertha_v4_2.brd, Bertha_v4_2.sch, Bertha_v4_3.brd, Bertha_v4_3.sch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]
2016-12-13 Added Comment not to solder I2C pull-ups closes #22
    [ph_v5.brd, ph_v5.sch]
2016-12-13 provided up to date pin mapping
    [PinMapping20161206.csv]
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2016-12-19 Added protection diode on 12V line closes #26
    [Bertha_v4_4.brd, Bertha_v4_4.sch]
2016-12-19 4mm holes on mainboard
    [Bertha_v4_4.brd]
2016-12-21 Added jack connector for PID closes #40
    [Bertha_v4_4.brd, Bertha_v4_4.sch]
2016-12-21 Changed pin Mapping to allow PWM food control Need to Adapat Arduino code !!!
    [Bertha_v4_4.brd, Bertha_v4_4.sch, PinMapping20161206.csv]
2016-12-21 Added Jack connector for DS18B20 closes #24
    [Bertha_v4_4.brd, Bertha_v4_4.sch]
2016-12-21 Changed DS18B20 package to MSOP8
    [Bertha_v4_4.brd, Bertha_v4_4.sch]
2016-12-21 regenerated gerbers for 4.4, displaying values
    [Bertha_v4_4.brd, Bertha_v4_4.sch]
2016-12-21 Heater contacts PCB closes #35 Check dimensions are ok
    [PID.GBL, PID.GBO, PID.GBP, PID.GBS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]
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2016-12-23 Changing LCD SPI communication protocol Modified files rights
    [PinMapping20161206.csv, StateMachines.csv, V4_PARAMS20161206.csv]
2017-01-06 First sketch under freecad
    [BASE_JUPE_FEMELLE.fcstd, BASE_JUPE_MALE.fcstd, Bioreactor_sketches.fcstd, Bioreactor_sketches_02.fcstd]
2017-01-06 work in progress
    [Bioreactor_sketches.fcstd]
2017-01-06 CAD v4.3 Freecad test
    [Bioreactor_sketches.fcstd]
2017-01-06 CAD test
    [Bioreactor_sketches.fcstd]
2017-01-06 fix front&back sides
    [Bioreactor_sketches.fcstd]
2017-01-06 Fix bugs on front side plate
    [Bioreactor_sketches.fcstd]
2017-01-08 Add bash script to generate BOM.tsv
    [BOM.tsv]
2017-01-08 Update BOM script
    [BOM.tsv]
2017-01-08 Correct first line
    [BOM.tsv]
2017-01-08 Fix spelling
    [BOM.tsv]
2017-01-09 FreeCAD update with DXF files for direct laser cutting
    [Bioreacteur_v4_4mm.dxf, Bioreacteur_v4_6mm.dxf, Bioreactor_sketches.fcstd]
2017-01-09 CAD update
    [Bioreactor_sketches_03.fcstd]
2017-01-09 update of DXF CAD
    [Bioreacteur_v4_6mm.dxf]
2017-01-09 CAD fixing
    [Bioreactor_sketches_04.fcstd]
2017-01-09 update DXF 4mm
    [Bioreacteur_v4_4mm.dxf]
2017-01-09 fixing dimensions
    [Bioreactor_sketches_04.fcstd]
2017-01-09 fix bugs on DXF
    [Bioreacteur_v4_6mm.dxf]
2017-01-09 CAD fixing peristatic pump screw angle
    [Bioreactor_sketches_04.fcstd]
2017-01-09 error message on BASE_PAROI_MALE_LCD
    [Bioreactor_sketches_04.fcstd]
2017-01-10 resolve error CAD
    [Bioreacteur_v4_6mm.dxf, Bioreactor_sketches_04.fcstd]
2017-01-10 big loading cell dimensions add
    [Bioreactor_sketches_04.fcstd]
2017-01-10 holes for electronic fixation
    [Bioreacteur_v4_6mm.dxf, Bioreactor_sketches_04.fcstd]
2017-01-10 Holes size reduced to 3.2mm fix #50 ref #39
    [Bertha_v4_4.brd]
2017-01-11 CAD hole stepper fix
    [Bioreactor_sketches_04.fcstd]
2017-01-11 CAD magnet holder for 3D printing
    [Stepper_magnet_holder.stl, Stepper_magnet_holder_01.FCStd]
2017-01-12 3D print for magnet holder test2
    [Bioreactor_sketches_04.fcstd, Stepper_magnet_holder.stl, Stepper_magnet_holder_01.FCStd]
2017-01-12 CAD pcb holes entry fix
    [Bioreactor_sketches_04.fcstd]
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2017-01-12 updated DXF files
    [Bioreacteur_v4_6mm.dxf, Bioreactor_sketches_04.fcstd]
2017-01-13 CAD fix on loading cell width & HX711 socket hole
    [Bioreactor_sketches_04.fcstd]
2017-01-13 CAD for Alu tank foundation
    [Tank_alu_foundation.FCStd]
2017-01-13 temperature sensor hole added
    [Bioreacteur_v4_6mm.dxf, Bioreactor_sketches_04.fcstd]
2017-01-13 fix alu foundation
    [Tank_alu_foundation.FCStd]
2017-01-13 another fix on alu foundations
    [Tank_alu_foundation.FCStd]
2017-01-13 pcb master holes fix
    [Bioreactor_sketches_04.fcstd]
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2017-01-16 fix on CAD magnet holder
    [Stepper_magnet_holder_01.FCStd]
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2017-01-25 fix socket entry closes #67
    [Bioreactor_sketches_04.fcstd]
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2017-01-27 corrected LED error on v4.4, PCB shortened by 1mm
    [Bertha_v4_4.brd]
2017-01-27 shortened boards by 1mm, closes #68
    [Bertha_v4_5.brd, ph_v6.brd]
2017-01-27 silk screen correction, need to optimize the current limiting resistors on 4.5
    [Bertha_v4_5.brd, Bertha_v4_5.sch]
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2017-01-30 correction on PID labelling, closes #71
    [Bertha_v4_4.brd, Bertha_v4_4.sch, Bertha_v4_5.brd]
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2017-02-05 corrected powerFET labelling
    [Bertha_v4_4.brd, Bertha_v4_4.sch, Bertha_v4_5.brd, Bertha_v4_5.sch]
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2017-04-12 Corrected minor mistakes on pull uo/down lines closes #90 , Gebers to be recreated
    [Bertha_v4_5.brd, Bertha_v4_5.sch]
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

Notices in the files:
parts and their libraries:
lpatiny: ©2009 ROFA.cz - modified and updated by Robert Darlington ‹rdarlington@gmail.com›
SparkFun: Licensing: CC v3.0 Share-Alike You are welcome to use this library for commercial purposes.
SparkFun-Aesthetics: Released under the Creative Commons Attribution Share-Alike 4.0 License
